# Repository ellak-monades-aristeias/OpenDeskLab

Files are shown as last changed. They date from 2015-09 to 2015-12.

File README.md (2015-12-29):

# OpenDeskLab




OpenDeskLab continuous documentation can be found in [Read the Docs](https://opendesklab.readthedocs.org/)

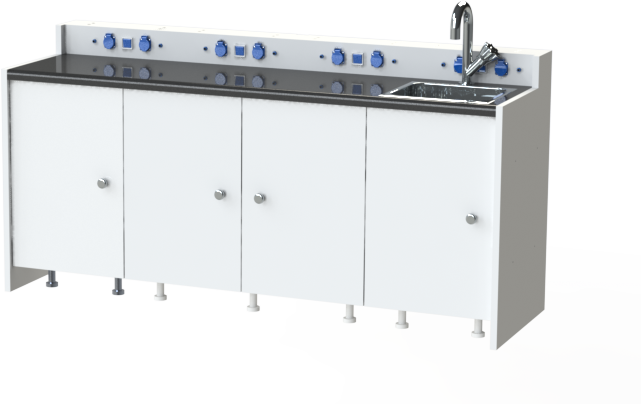
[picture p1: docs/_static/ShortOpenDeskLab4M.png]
OpenDeskLab


## Σύντομη Περιγραφή

Τα γραφεία εργαστηρίων σχολικών μονάδων φυσικών επιστημών είναι μια ειδική κατηγορία πάγκων εργασίας που έχουν στόχο την εξυπηρέτηση της διεξαγωγής των εργαστηρίων φυσικής, χημείας, βιολογιάς, γεωλογίας και γεωγραφίας. Οι ανάγκες των εργαστηριών αυτών διαφέρουν σημαντικά, αλλά έχουν κοινό γνώμονα ότι στοχεύουν να προστατεύουν τους ανήλικους μαθητές από ατυχήματα που μπορεί να συμβούν κατά την διεξαγωγή των πειραμάτων. Ταυτόχρονα, παρέχουν ευκολίες για την πραγματοποίηση των εργαστηρίων, όπως η ασφαλής παροχή ηλεκτρικού ρεύματος (εναλλασσόμενου και συνεχούς), η παροχή και αποχέτευση ρευστών (αέριων και υγρών) καθώς και η εύκολη πρόσβαση σε συστήματα ασφαλείας (πυρόσβεση/ηλεκτρικές ασφάλειες).

## Τεχνικά στοιχεία πρότασης
Το OpenDeskLab αποτελεί μία πρόταση για ένα παραμετροποιήσιμο γραφείο εργαστηρίων που μπορεί να διαμορφωθεί κατάλληλα ανάλογα με τις (εργαστηριακές) απαιτήσεις και τον διαθέσιμο χώρο. Το OpenDeskLab είναι σύμφωνο με τους κανονισμούς ασφαλείας όπως ορίζονται από τους Ελληνικούς κανονισμούς, και με υψηλή ποιότητα ώστε να εξυπηρετεί τις ανάγκες χωρίς να απαιτεί υψηλό κόστος συντήρησης. Ταυτόχρονα, θα χρησιμοποιεί φιλικά προς το περιβάλλον υλικά και θα διατηρεί χαμηλό κόστος κατασκευής, βοηθώντας την εξάπλωση του σε όλα τα δημόσια και ιδιωτικά εκπαιδευτήρια, φέρνοντας την πειραματική διδασκαλία κοντά σε όλους τους μαθητές.

Το OpenDeskLab διαθέτει

* __Αρθρωτή δομή,__ ώστε να διατηρείται το κόστος κατασκευής το χαμηλότερο δυνατό για τις ανάγκες που χρειάζονται
* __Παραμετροποιήσιμες διαστάσεις,__ ώστε να εκμεταλεύεται βέλτιστα τον χώρο του εργαστηρίου
* __Παροχή ηλεκτρικού ρεύματος,__ για την εύκολη διεξαγωγή πειραμάτων που χρειάζονται ηλεκτρική ισχύ
* __Παροχή και αποχέτευση νερού,__ για την εύκολη πρόσβαση στον καλύτερο διαλύτη της φύσης
* __Παροχή και αποχέτευση αέρα,__ για την εύκολη πρόσβαση σε αέρα υπό πίεση
* __Αποθηκευτικούς χώρους,__ για την φύλαξη των επικίνδυνων υλικών
* __Εξαερισμό,__ για την αποχέτευση αέριων παράγωγων από την αίθουσα
* __Ασφάλεια,__ για την προστασία των μαθητών μέσω πυρόσβεσης, ηλεκτρικών ρελέ, και χημικά ανενεργών υλικών κατασκευής

Συγκεκριμένα, το OpenDeskLab δίνει την δυνατότητα στους κατασκευαστές του να το παραμετροποιήσουν πλήρως στις ανάγκες τους, είτε αυτές είναι ο χώρος διεξαγωγής πειραμάτων ενός σχολείου είτε ένας εργαστηριακός χώρος ενός [hackerspace](https://en.wikipedia.org/wiki/Hackerspace) ή [fablab](https://en.wikipedia.org/wiki/Fab_lab). Η αρθρωτή δομή του επιτρέπει να δομηθεί είτε ως ηλεκτρολογικός πάγκος, είτε ως χημικός πάγκος, είτε ως πάγκος γενικών εργασιών. Σαν ηλεκτρολογικός πάγκος, διαθέτει παροχές συνεχούς και εναλλασσόμενου ρεύματος αλλά και εύκολες συνδέσεις μετρητικών (παλμογράφων/πολυμέτρων), με ηλεκτρολογικές ασφάλειες και ρελέ. Σαν χημικός πάγκος, διαθέτει παροχή αέρα και νερού, αποχέτευση, κάδο αποβλήτων και αποθηκευτικό χώρο για επικίνδυνα υλικά και υλικά που φθείρονται από την έκθεση σε φωτισμό. Τέλος, σαν πάγκος γενικής χρήσης παρέχει φωτισμό, παροχή ισχύος για εργαλεία, παροχή πεπιεσμένου αέρα, προστασία μέσω πυρόσβεσης και εξαερισμού για την σκόνη και τον καπνό (από κολλήσεις ή άλλες διεργασίες).

### Καινοτομία, ανάλογες λύσεις και χρησιμότητα
Στην αγορά αυτή την στιγμή υπάρχουν πολλές εταιρίες που παρέχουν έτοιμες ή και προσαρμοσμένες λύσεις για εργαστηριακά γραφεία σχολικών εγκαταστάσεων \[[vasileiou](http://www.basileiou.com/), [psa](http://www.psalaboratoryfurniture.com/), [rizos](http://rizos.com.gr/epipla-ergastiriou-epiplwsi.html), [ecofarm](http://www.ecofarm.net/plist.php?cat_id=24), [kertus](http://www.kertus.gr/pharmacists/index.php?option=com_k2&view=itemlist&task=category&id=80:%CE%AD%CF%80%CE%B9%CF%80%CE%BB%CE%B1-%CE%B5%CF%81%CE%B3%CE%B1%CF%83%CF%84%CE%B7%CF%81%CE%AF%CE%BF%CF%85&lang=el)\]. Το κόστος αυτών όμως είναι ιδιαιτέρως αυξημένο, καθώς αναφέρονται σε ένα προϊόν που έχει περιορισμένο κοινό και αυξημένες απαιτήσεις ασφαλείας. Τα μεγαλύτερα ιδιωτικά εκπαιδευτήρια της Ελλάδας, δεν χρησιμοποιούν γραφεία ειδικά σχεδιασμένα για την διεξαγωγή εργαστηρίων φυσικών επιστημών, καθώς ακόμα και για αυτά, το κόστος αγοράς τους είναι απαγορευτικό. Στα δημόσια εκπαιδευτήρια, από την άλλη, οι εργαστηριακοί χώροι που διατίθενται για τους μαθητές είναι λιγότεροι από 100 για όλη την χώρα, πράγμα που αναλογεί σε πολύ λίγα λεπτά εργαστηριακού χρόνου για κάθε μαθητή.

Το OpenDeskLab είναι το πρώτο ανοιχτό γραφείο εργαστηριακών πειραμάτων, και έχει στόχο να αποτελέσει το έναυσμα ώστε να διαδοθεί η τεχνογνωσία για τον εξοπλισμό και την κατασκευή ανοιχτών εργαστηρίων σε όλο τον κόσμο, τηρώντας τα διεθνή πρότυπα ασφαλείας. 

### Κοινωνικά Οφέλη
Με κύριο στόχο τον περιορισμό του κόστους λειτουργίας αλλά και του κόστους ανέγερσης νέων σχολικών μονάδων, δεδομένης της δύσκολης οικονομικής κατάστασης της χώρας, το Υπουργείο Παιδείας το 2012 όρισε την δημιουργία των ΕΚΦΕ (Εργαστηριακά Κέντρα Φυσικών Επιστημών). Τα ΕΚΦΕ έχουν στόχο την τεχνική και οργανωτική υποστήριξη της εργαστηριακής διδασκαλίας των φυσικών μαθημάτων \[[ΦΕΚ](http://edu.klimaka.gr/arxeio/nomothesia-fek/fek-2314-2012-epilogh-ypevthynoi-scholikes-drasthriothtes-klimaka.pdf)\]. Σε κάθε Διεύθυνση Δευτεροβάθμιας εκπαίδευσης λειτουργεί ένα τουλάχιστον ΕΚΦΕ, ενώ στις πυκνοκατοικημένες περιοχές λειτουργούν περισσότερα ΕΚΦΕ με στόχο να εξυπηρετούν καλύτερα τα πολλά σχολεία της περιοχής. Συνολικά στην Ελλάδα λειτουργούν 78 ΕΚΦΕ, εκ των οποιών τα 15 βρίσκονται στον νομό Αττικής ενώ σε πολλούς νομούς της Ελλάδας υπάρχει μόνο ένα ΕΚΦΕ για να εξυπηρετεί όλα τα σχολεία που συχνά βρίσκονται απομακρυσμένα από αυτό.

Το πάγιο κόστος ενός Εργαστηριακού Κέντρου Φυσικών Επιστημών είναι υψηλό, καθώς απαιτεί εργαστηριακό εξοπλισμό υψηλού κόστους, ηλεκτρονικούς υπολογιστές και ειδικές πειραματικές διατάξεις. Το κόστος χρήσης από την άλλη αποτελείται από το κόστος των εργαζομένων καθώς και τα αναλώσιμα απαραίτητα για την διεξαγωγή των εργαστηρίων. Τέλος, πρέπει να συμπεριληφθεί και το κόστος συντήρησης των εγκαταστάσεων, ηλεκτροδότησης, τηλεπικοινωνιών και υδροδότησης.

Με την ανάπτυξη του OpenDeskLab, δύναται στα σχολεία να διαθέτουν δικό τους εργαστηριακό χώρο, με χαμηλό κόστος χωρίς να χρειάζεται να συντηρούνται τα ΕΚΦΕ και χωρίς να αυξάνεται το κόστος χρήσης προς το Υπουργείο Παιδείας. Όλα τα ιδρύματα δευτεροβάθμιας εκπαίδευσης έχουν εκπαιδευμένο προσωπικό για την διεξαγωγή πειραμάτων (καθηγητές φυσίκης, χημείας κλπ). Επίσης, το κόστος των αναλωσίμων που απαιτούνται για την πραγματοποίηση των εργαστηρίων συνολικά δεν αλλάζει, καθώς θα διεξάγεται ο ίδιος αριθμός εργαστηριακών ασκήσεων.

## Σε ποίους απευθύνεται

### Κοινότητες Χρηστών
Το OpenDeskLab απευθύνεται σε όλους τους εργαστηριακούς χώρους, είτε πρόκειται για σχολικές εγκαταστάσεις είτε ανοιχτές κοινότητες makers, όπως hackerspaces, makerlabs, fablabs κλπ. 

### Κοινότητες Κατασκευαστών
Οι κατασκευαστές που ενδιαφέρονται να αναπτύξουν/επεκτείνουν το έργο, προτείνεται να έχουν γνώσεις πάνω στην κατασκευή επίπλων ή τον μηχανολογικό σχεδιασμό, πρόσβαση σε κάποιο ανοιχτό ή κλειστό πρόγραμμα τρισδιάστατου σχεδιασμού και γνώσεις της πλατφόρμας Sphinx (σύνταξη κειμένου σε Restructured Text).

Βεβαίως, ενθαρρύνονται όλες οι προτάσεις για περαιτέρω βελτίωση του έργου ακόμα και από απλούς χρήστες που παρατήρησαν κάποια έλλειψη ή κάποια δυσλειτουργία του OpenDeskLab, με την χρήση των issues.

## Κόστος

Όσον αφορά το κόστος, το OpenDeskLab μπορεί να παραμετροποιηθεί με πολλούς διαφορετικούς τρόπους, μεταβάλλοντας σημαντικά το τελικό κόστος του ανά μονάδα. Το πιο ακριβό κομμάτι του είναι το [Hazardous Materials Cabinet](https://opendesklab.readthedocs.org/en/latest/include/parts/hazardous_materials_cabinet.html#bill-of-materials), που στοιχίζει περίπου 226 euro. Από την άλλη το [Drawer Cabinet](https://opendesklab.readthedocs.org/en/a/include/parts/drawer_cabinet.html#bill-of-materials) κοστίζει μόλις 56 euro, το [Double Cabinet](https://opendesklab.readthedocs.org/en/latest/include/parts/double_cabinet.html#bill-of-materials) μόνο 57 euro και το [Single Cabinet](https://opendesklab.readthedocs.org/en/latest/include/parts/single_cabinet.html#bill-of-materials) μόλις 40 euro. Τα επιπρόσθετα κομμάτια που είναι απαραίτητα για το OpenDeskLab κοστίζουν σαφώς λιγότερο, για παράδειγμα το [Short Desk Back](https://opendesklab.readthedocs.org/en/latest/include/parts/desk_back.html#id3) ξεκινάει περίπου στα 39 euro και μπορεί να φτάσει τα 82 euro για την έκδοση Tall, ενώ τα [Side Panels](https://opendesklab.readthedocs.org/en/latest/include/parts/desk_side.html#id3) κοστίζουν 22 ή 33 euro το ζευγάρι, για την short ή την tall έκδοση αντίστοιχα. 

Τα πιο ακριβά απαραίτητα κομμάτια του OpenDeskLab είναι τα ηλεκτρικά και πνευματικά φις του [Cable Routing](https://opendesklab.readthedocs.org/en/latest/include/parts/cable_routing.html#bill-of-materials), που ξεκινούν από τα 78 euro και μπορούν να φτάσουν τα 131 euros. Το κομμάτι [Worktop](https://opendesklab.readthedocs.org/en/latest/include/parts/worktop.html#bill-of-materials) από την άλλη πλευρά κοστίζει από 33 euro μέχρι περίπου 56 euro έκαστο (για διαφορετικές διαστάσεις).

Τα ανωτέρω κόστη είναι υπολογισμένα σύμφωνα με τις τιμές των πρώτων υλών, και ενδέχεται να διαφέρουν στην περίπτωση που η διαμόρφωση της κατασκευής (ή η ποσότητα των κατασκευαζόμενων γραφείων) αφήνει μεγάλο περίσσευμα πρώτης ύλης ανεκμετάλευτο (φύλλα μελαμίνης, πάγκος εργασίας, βίδες κλπ).

Για την κατασκευή των φύλλων μελαμίνης χρείαζεται πρόσβαση σε εργαλειομηχανή κατεργασίας ξύλου αριθμητικού ελέγχου. Για την συναρμολόγηση του γραφείου, ανάλογα με την διαμόρφωση του, χρειάζονται ελάχιστα εργαλεία, θεωρώντας ότι τα φύλλα είναι ήδη επεξεργασμένα και οι οπές γίνανε από την εργαλειομηχανή σε προηγούμενο στάδιο.

## Χρονοδιάγραμμα
| Ημερομηνίες	| Διάρκεια | Περιγραφή Εργασιών 																		|
|---------------|----------|--------------------------------------------------------------------------------------------|
| 17/09 - 21/09 | 3 Ημ.    | Συγκέντρωση προδιαγραφών και απαιτήσεων, μελέτη των κανονισμών ασφαλείας 					|
| 22/09 - 02/10 | 9 Ημ.    | Αναλυτικός σχεδιασμός, μελέτη εργονομίας και λειτουργικότητας, σχεδιασμός για συναρμολόγηση|
| 05/10 - 09/10 | 5 Ημ.    | Κοστολόγιση και πίνακας υλικών (Bill of Materials) 										|
| 12/10 - 15/10 | 4 Ημ.  | Συγγραφή της τεκμηρίωσης και αναλυτικών οδηγιών κατασκευής 								    |

## Παραδοτέα
Στα πλαίσια των αρχών του ανοιχτού υλισμικού, τα παραδοτέα της πρότασης θα διατεθούν με άδεια Creative Commons. Ταυτόχρονα, όπου γίνεται θα προτιμηθούν τα ανοιχτά πρότυπα, χωρίς όμως να αποτελέσουν περιοριστικό παράγοντα για την κατασκευή και την εξάπλωση του OpenDeskLab. Με βασικό κριτήριο την ευκολία κατασκευής αλλά και την συμβατότητα με τα καθιερωμένα προγράμματα σχεδιασμού, τα αρχεία θα διατεθούν σε μορφή [STEP](https://en.wikipedia.org/wiki/ISO_10303-21), [DWG](https://en.wikipedia.org/wiki/.dwg) και δισδιάστατου [DXF](https://en.wikipedia.org/wiki/AutoCAD_DXF) για να είναι εύκολα κατασκευάσιμα από μηχανές αριθμητικού ελέγχου (CNC), αλλά και σε μορφή διαστασιολογημένων PDF για να κατασκευάζεται με απλά ηλεκτρικά εργαλεία χωρίς να απαιτείται πρόσβαση σε ακριβές εργαλειομηχανές.

| Τίτλος Παραδοτέου 													| Url     |
|-----------------------------------------------------------------------|---------|
| Τεχνική αναφορά με τις προδιαγραφές και τους κανονισμούς ασφαλείας 	| [source](https://github.com/ellak-monades-aristeias/OpenDeskLab/blob/master/docs/include/specifications.rst), [html](https://opendesklab.readthedocs.org/en/latest/include/specifications.html)  |
| Παραμετρικά σχέδια κατασκευής και εικόνες, μελέτη εργονομίας 			| [folder](https://github.com/ellak-monades-aristeias/OpenDeskLab/tree/master/docs/_static), [html](https://opendesklab.readthedocs.org/en/latest/include/modules.html#module-list), [grabcad](https://grabcad.com/library/opendesklab-2) |
| Σχέδια για συναρμολόγηση												| [videos](https://github.com/ellak-monades-aristeias/OpenDeskLab/tree/master/docs/_static), [OpenDeskLab html](https://opendesklab.readthedocs.org/en/latest/include/modules.html), [Cable Routing html](https://opendesklab.readthedocs.org/en/latest/include/parts/cable_routing.html#assembly-procedure), [Double Cabinet html](https://opendesklab.readthedocs.org/en/latest/include/parts/double_cabinet.html#assembly-procedure), [Drawer Cabinet html](https://opendesklab.readthedocs.org/en/latest/include/parts/drawer_cabinet.html#assembly-procedure), [Hazardous Materials Cabinet html](https://opendesklab.readthedocs.org/en/latest/include/parts/hazardous_materials_cabinet.html#assembly-procedure), [Sink Cabinet html](https://opendesklab.readthedocs.org/en/latest/include/parts/sink_cabinet.html#assembly-procedure) |
| Τεκμηρίωση και τεχνική αναφορά οδηγιών κατασκευής						| [Read The Docs](https://opendesklab.readthedocs.org/en/latest/index.html) |

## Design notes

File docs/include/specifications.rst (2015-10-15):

=============================
Specifications & Requirements
=============================

According to the rules and regulations of the EU_ and most International Standards committees, there are some safety rules that must be taken into account for manufacturing laboratory equipment. However, although OpenDeskLab is designed according to those rules, it must be noted that the authors and creators of OpenDeskLab are **not** eligible for any kind of damage that may happen while building or using the desk. A laboratory that is used in professional environments **must** be certified by an authorized person, and OpenDeskLab is neither certified nor can fullfil all the regulations of every standard in the world.

.. warning::

    OpenDeskLab is not certified for professional use. The authors are not eligible for any damage that may occur while building or using the product.

:index:`Safety`
---------------

- Central ventilation is required in laboratory facilities
- Water tap within 15 meters or 10 seconds of the users
- Chemical storage must have edges protected for spillage
- Flammable materials must be stored in UL/NFPA certified storage areas
- Acids and bases must be stored separately
- Compressed air canisters must me fixed securely with fire resistant strands
- Toxic wastes must be handled according to specific regulations
- All storage areas must be clearly signed
- Labels must be placed for

    - Water
    - Electricity
    - Chemicals
    - Flammables
    - Acids/Bases

:index:`Specifications`
-----------------------

OpenDeskLab is comprised of the following modules:

- :doc:`parts/cable_routing`
- :doc:`parts/desk_back`
- :doc:`parts/desk_side`
- :doc:`parts/double_cabinet`
- :doc:`parts/drawer_cabinet`
- :doc:`parts/hazardous_materials_cabinet`
- :doc:`parts/lighting`
- :doc:`parts/single_cabinet`
- :doc:`parts/sink_cabinet`
- :doc:`parts/worktop`

These can be combined in any desirable way to formulate a -- three, four or five module wide -- self-contained laboratory desk. 

:index:`Materials`
------------------

    .. tabularcolumns:: |c|c|
    .. table:: 

        ======================= ==================
         **OpenDeskLab Materials**
        ------------------------------------------
        Melamine                Electric Plug
        Plywood                 Electric Cable
        Cam Lock                Pneumatic Coupling
        Cam Bolt                Pneumatic Tubing
        Wooden Dowel Pin        Sink
        Concealed Hinge         Water Tap
        Hinge Mounting Plate    Hydraulic Hose
        Plastic Adjustable Leg  Plastic Tube
        Metal Adjustable Leg    Silicone Caulk
        Knob                    LED Lighting
        Electric Switch         Insulating Tape
        Intumescent Paint       
        ======================= ==================

.. _EU: https://en.wikipedia.org/wiki/European_Union

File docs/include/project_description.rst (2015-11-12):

============================
Project :index:`Description`
============================



OpenDeskLab aims at creating an open design for laboratory desks that is

- Modular structure
- Reconfigurable dimensions
- Safe
- Easy to build
- Low cost
- Highly functional

The material used for the structure of is mostly melamine boards, that can be precut by any CNC supplier to the given dimensions. The assembly of an OpenDeskLab is designed so as to require only the basic of the tools, such as a Pozidriv screwdriver. The desk itself can be configured in many different ways, and the materials as well as the aesthetics can be customized according to the owners taste.

All the materials chosen for the OpenDeskLab (and their respective sockets) are dimensioned according to the International standards and can be sourced online or in many local stores. The desk can be assembled easily, following the instructive videos provided for each component. Various components are provided, although anyone can design his own component to pair with the already developed ones.

OpenDeskLab can be built in three, four and five module variants. The builder may choose the modules that will form his desk according to his needs, and the modular design will accommodate every customization (with some minor limitations) possible. 

:index:`Applications`
---------------------

The main audience that OpenDeskLab targets are high school laboratories and home/diy/hackerspace/fablab places. Due to its' modular nature, OpenDeskLab can be used in a variety of applications, including (but not limited to) electrical, chemical and general use workbenches. It can provide electrical as well as gas connections, water supply and drain and of course ventilation. A hazardous materials storage is also provided that is the only fully self-contained module that can provide a safe storage for chemicals and flammables.  

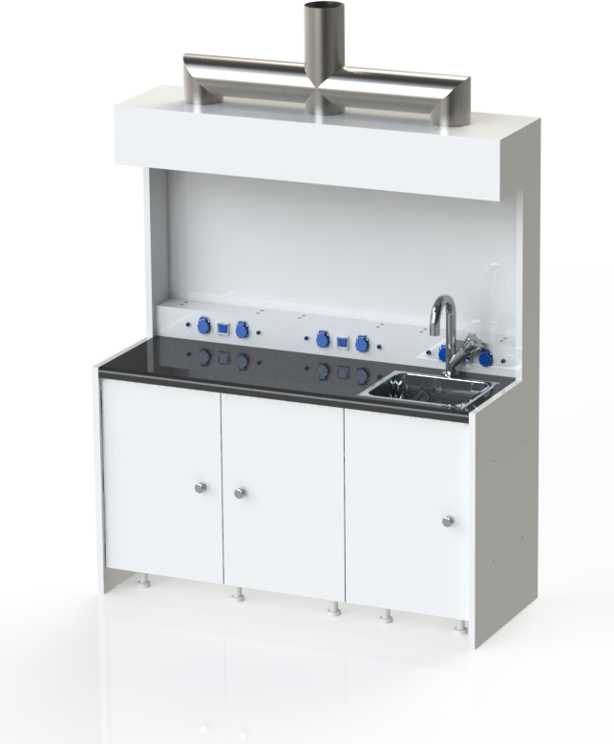
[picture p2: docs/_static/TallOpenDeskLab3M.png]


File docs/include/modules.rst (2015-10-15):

============================
:index:`Modules`
============================

OpenDeskLab is comprised of different modules that can be assembled following some basic guidelines.

Assembly Procedure
~~~~~~~~~~~~~~~~~~

The modules are assembled together using M6 connecting screws through the four holes that exist in every module.

.. raw:: html 

   <video src="../_static/OpenDeskLab3M.ogv" width="696" type="video/ogg" controls="controls">
   Your browser does not support the video tag.
   </video>

Drawings
~~~~~~~~

:download:`Tall OpenDeskLab </_static/OpenDeskLab3M.pdf>`

:download:`Short OpenDeskLab </_static/OpenDeskLabShort4M.pdf>`

+-------------------------------------+--------------------------------------+--------------------------------------+
| OpenDeskLab modules with bakelite doors                                                                           |
+=====================================+======================================+======================================+
| 
|                                     |                                      |                                      |
| (a) :doc:`parts/single_cabinet`     | (b) :doc:`parts/double_cabinet`      | (c) :doc:`parts/drawer_cabinet`      |
+-------------------------------------+--------------------------------------+--------------------------------------+

Module List
~~~~~~~~~~~

.. toctree::
   :maxdepth: 1
   
   parts/cable_routing
   parts/desk_back
   parts/desk_side
   parts/double_cabinet
   parts/drawer_cabinet
   parts/hazardous_materials_cabinet
   parts/lighting
   parts/single_cabinet
   parts/sink_cabinet
   parts/worktop

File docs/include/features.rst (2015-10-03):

=================
:index:`Features`
=================

.. toctree::
   
   parts/single_cabinet
   parts/double_cabinet
   parts/drawer_cabinet
   parts/sink_cabinet
   parts/hazardous_materials_cabinet
   parts/cable_routing
   parts/top_mount_lighting
   parts/top_mount_ventilation
   parts/worktop

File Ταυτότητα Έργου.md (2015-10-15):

# Ταυτότητα Έργου

OpenDeskLab

## Περιγραφή του Έργου
Το OpenDeskLab αποτελεί μία πρόταση για ένα παραμετροποιήσιμο γραφείο εργαστηρίων που μπορεί να διαμορφωθεί κατάλληλα ανάλογα με τις (εργαστηριακές) απαιτήσεις και τον διαθέσιμο χώρο. Το OpenDeskLab είναι σύμφωνο με τους κανονισμούς ασφαλείας όπως ορίζονται από τους Ελληνικούς κανονισμούς, και με υψηλή ποιότητα ώστε να εξυπηρετεί τις ανάγκες χωρίς να απαιτεί υψηλό κόστος συντήρησης. Ταυτόχρονα, χρησιμοποιεί φιλικά προς το περιβάλλον υλικά και διατηρεί χαμηλό κόστος κατασκευής, βοηθώντας την εξάπλωση του σε όλα τα δημόσια και ιδιωτικά εκπαιδευτήρια, φέρνοντας την πειραματική διδασκαλία κοντά σε όλους τους μαθητές.

Η αρθρωτή δομή του επιτρέπει να δομηθεί είτε ως ηλεκτρολογικός πάγκος, είτε ως χημικός πάγκος, είτε ως πάγκος γενικών εργασιών. Σαν ηλεκτρολογικός πάγκος, διαθέτει παροχές συνεχούς και εναλλασσόμενου ρεύματος. Σαν χημικός πάγκος, διαθέτει παροχή αέρα και νερού, αποχέτευση, κάδο αποβλήτων και αποθηκευτικό χώρο για επικίνδυνα υλικά και υλικά που φθείρονται από την έκθεση σε φωτισμό. Τέλος, σαν πάγκος γενικής χρήσης παρέχει φωτισμό, παροχή ισχύος για εργαλεία, παροχή πεπιεσμένου αέρα και εξαερισμού για την σκόνη και τον καπνό (από κολλήσεις ή άλλες διεργασίες).

## Χρησιμότητα
Τα μεγαλύτερα ιδιωτικά εκπαιδευτήρια της Ελλάδας, δεν χρησιμοποιούν γραφεία ειδικά σχεδιασμένα για την διεξαγωγή εργαστηρίων φυσικών επιστημών, καθώς ακόμα και για αυτά, το κόστος αγοράς τους είναι απαγορευτικό. Στα δημόσια εκπαιδευτήρια, από την άλλη, οι εργαστηριακοί χώροι που διατίθενται για τους μαθητές είναι λιγότεροι από 100 για όλη την χώρα, πράγμα που αναλογεί σε πολύ λίγα λεπτά εργαστηριακού χρόνου για κάθε μαθητή.

Το OpenDeskLab είναι το πρώτο ανοιχτό γραφείο εργαστηριακών πειραμάτων, και έχει στόχο να αποτελέσει το έναυσμα ώστε να διαδοθεί η τεχνογνωσία για τον εξοπλισμό και την κατασκευή ανοιχτών εργαστηρίων σε όλο τον κόσμο, τηρώντας τα διεθνή πρότυπα ασφαλείας. 

## Ελάχιστες Απαιτήσεις
Το OpenDeskLab χρησιμοποιεί σαν πρώτη ύλη μελαμίνη πάχους 18 και 25 χιλιοστών. Για το μεγαλύτερο μέρος των συνδέσμων του χρησιμοποιεί έκκεντρα φεράμια που επιτρέπουν την εύκολη συναρμολόγηση και αποσυναρμολόγηση του πάγκου και των αποθηκευτικών χώρων χωρίς την χρήση πολύπλοκων εργαλείων.

Για την τεκμηρίωση όλου του έργου χρησιμοποιήθηκε η πλατφόρμα Sphinx, και το σύστημα συνεχούς τεκμηρίωσης [Read the Docs](http://www.readthedocs.org). Τα σχέδια υλοποιήθηκαν στο [SolidWorks 2016](http://www.solidworks.com), ενώ διατίθενται ελεύθερα μέσω της πλατφόρμας [GrabCAD](http://www.grabcad.com), μέσα από την οποία μπορεί κάποιος να τα μεταφορτώσει σε οποιοδήποτε ουδέτερο πρότυπο CAD αρχείων (STEP, IGES, STL).

## Αποθετήριο
Το αποθετήριο μπορεί να βρεθεί στο [github](https://github.com/ellak-monades-aristeias/OpenDeskLab), η τεκμηρίωση του στο [Read the Docs](http://opendesklab.readthedocs.org) ενώ τα τρισδιάστατα μοντέλα CAD στο [GrabCAD](http://www.grabcad.com/library/opendesklab-2) υπό την άδεια χρήσης [CC BY-SA 4.0](https://creativecommons.org/licenses/by-sa/4.0/).

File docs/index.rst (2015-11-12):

.. OpenDeskLab documentation master file, created by
   sphinx-quickstart on Wed Sep 30 19:01:20 2015.
   You can adapt this file completely to your liking, but it should at least
   contain the root `toctree` directive.

=======================================
Welcome to OpenDeskLab's documentation!
=======================================

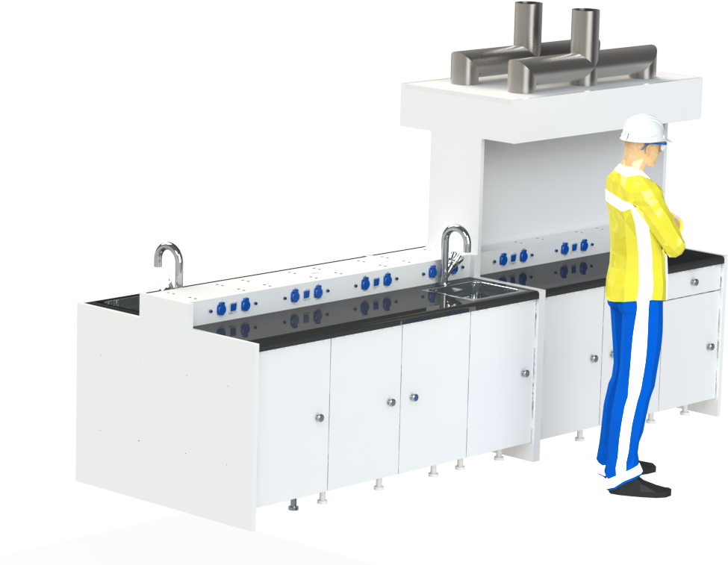
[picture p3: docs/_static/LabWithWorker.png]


.. toctree::
   :maxdepth: 2
   :glob:

      Project Description <include/project_description>
      Specifications <include/specifications>
      Modules <include/modules>
      Open Data <include/open_data>
      Acknowledgments <include/acknowledgments>

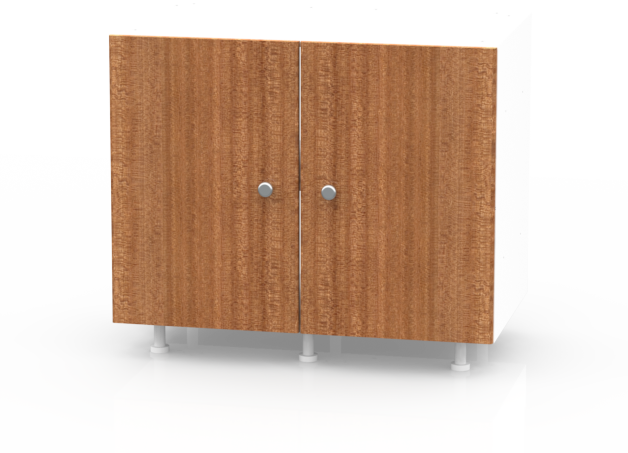
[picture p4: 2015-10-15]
docs/_static/wood/double.png

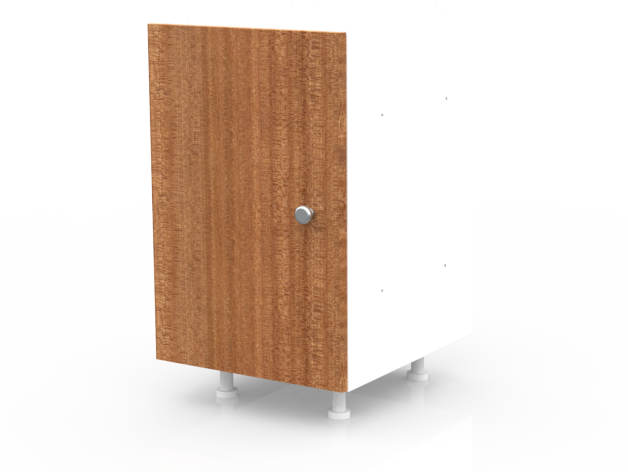
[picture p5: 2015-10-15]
docs/_static/wood/single.png

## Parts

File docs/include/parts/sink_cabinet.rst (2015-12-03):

:index:`Sink Cabinet`
---------------------

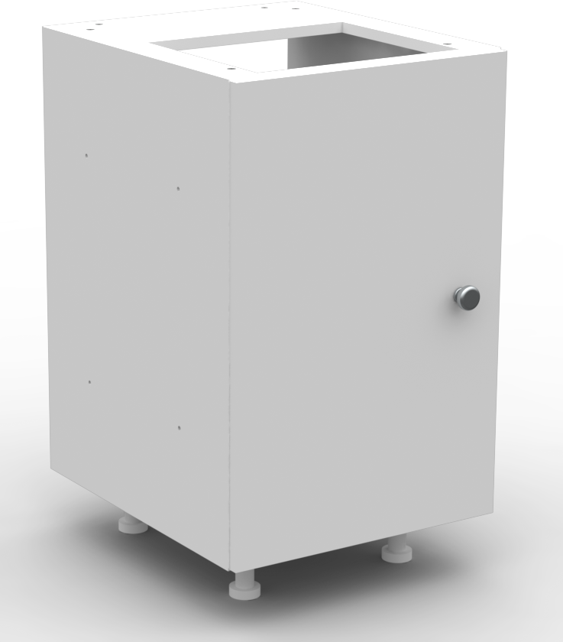
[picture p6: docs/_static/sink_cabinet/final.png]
sink cabinet


The sink cabinet is very similar to the :doc:`single_cabinet` module, however, the top shelf has a precut hole for the installation of the sink and the tap.

Although there are standard sizes for sinks and taps in the industry, most manufacturers tend to not follow them, for design reasons. This cabinet is designed for a 375x317 sink, which is a small standard sink size, however, in the case were the builder wants to use different sink size, he can choose to cut the hole using a jigsaw.

.. important::

    Tools Needed:
     - Pozidriv Screwdriver
     - Electric Screwdriver for the four plastic legs
     - Wrench
     - Jigsaw (Optional)

Assembly Procedure
~~~~~~~~~~~~~~~~~~

The assembly procedure is very simple, first you assemble the two side panels using the Cam Bolts and the Wooden Dowel Pins, and then you mount the Hinge Mounting Plates on the left or right side panel, according to your preference. (Mind there are fewer holes in the sink side panels)

.. raw:: html 

   <video src="../../_static/side_panel_assembly.ogv" width="696" type="video/ogg" controls="controls">
   Your browser does not support the video tag.
   </video>

Then you create the door assembly by mounting the Concealed Hinges with the provided screws (3.5mm x 16mm) and lastly you screw in the Knob.

.. raw:: html 

   <video src="../../_static/door_assembly.ogv" width="696" type="video/ogg" controls="controls">
   Your browser does not support the video tag.
   </video>   

Lastly you assemble them all together. The sink must be installed **after** the worktop is placed.

.. raw:: html 

   <video src="../../_static/sink_cabinet/Sink_Cabinet.ogv" width="696" type="video/ogg" controls="controls">
   Your browser does not support the video tag.
   </video>

Drawings
~~~~~~~~

:download:`Shelf </_static/single_cabinet/Melamine_Shelf.pdf>`

:download:`Top </_static/sink_cabinet/Sink_Melamine_Top.pdf>`

:download:`Side </_static/sink_cabinet/Sink_Melamine_Side.pdf>`

:download:`Sink Cabinet </_static/sink_cabinet/Sink_Cabinet.pdf>`

Bill of Materials
~~~~~~~~~~~~~~~~~

   .. tabularcolumns:: |l|c|c|c|
   .. table::

      +------------------------------------+----------+-----------+-------------+
      | Sink Cabinet - Bill of Materials                                        |
      +------------------------------------+----------+-----------+-------------+
      | Item                               | Quantity | Price/Pcs | Total Price |
      +====================================+==========+===========+=============+
      | Cam Lock 15mm x 12.5mm             |    12    |    0.148€ |      1.776€ |
      +------------------------------------+----------+-----------+-------------+
      | Cam Bolt 6mm x 45.5mm              |     8    |    0.880€ |      7.040€ |
      +------------------------------------+----------+-----------+-------------+
      | Wooden Dowel Pin 8mm x 30mm        |    12    |    0.029€ |      0.348€ |
      +------------------------------------+----------+-----------+-------------+
      | Concealed Hinge (9mm Overlay)      |     2    |    1.690€ |      3.380€ |
      +------------------------------------+----------+-----------+-------------+
      | Hinge Mounting Plate               |     2    |    0.980€ |      1.960€ |
      +------------------------------------+----------+-----------+-------------+
      | Plastic Adjustable Legs 100mm      |     4    |    0.750€ |      3.000€ |
      +------------------------------------+----------+-----------+-------------+
      | M6 x 40 Connecting Screws          |     4    |    0.753€ |      3.012€ |
      +------------------------------------+----------+-----------+-------------+
      | Melamine 18mm                      |  1.750   | 6.718€/m2 |     11.759€ |
      +------------------------------------+----------+-----------+-------------+
      | Door Knob                          |     1    |    1.080€ |      1.080€ |
      +------------------------------------+----------+-----------+-------------+
      | **Total Cost**                                            |     33.355€ |
      +------------------------------------+----------+-----------+-------------+

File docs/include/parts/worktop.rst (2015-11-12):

:index:`Worktop`
----------------

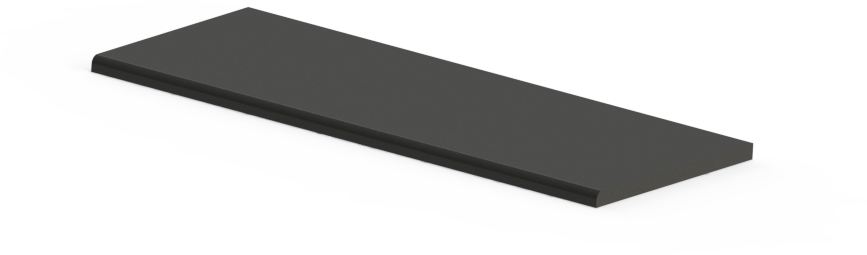
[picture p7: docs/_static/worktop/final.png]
worktop


.. important::

   Tools Needed:
    - Electric Screwdriver

Assembly Procedure
++++++++++++++++++

The worktop is assembled by simply screwing the top side of the cabinets with it, using the Pozidriv 3.5mm x 35mm screws. You open the doors of the cabinets, lie down on them and using an electric screwdriver you secure it in place.

If you have installed a sink cabinet module, you must also securely attach it to the worktop following the instructions provided by the sink.

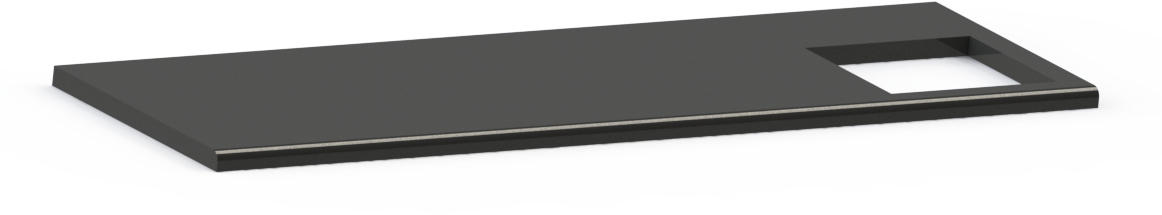
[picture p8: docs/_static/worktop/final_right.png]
worktop right


Drawings
++++++++

:download:`Worktop 3M </_static/worktop/Worktop_3M.pdf>`

:download:`Worktop Left Sink 3M </_static/worktop/Worktop_Left_Sink_3M.pdf>`

:download:`Worktop Right Sink 3M </_static/worktop/Worktop_Right_Sink_3M.pdf>`

Bill of Materials
+++++++++++++++++

   .. tabularcolumns:: |l|c|c|c|
   .. table::

      +------------------------------------+----------+-----------+-------------+
      | Worktop 3M - Bill of Materials                                          |
      +------------------------------------+----------+-----------+-------------+
      | Item                               | Quantity | Price/Pcs | Total Price |
      +====================================+==========+===========+=============+
      | Pozidriv Screws 3.5mm x 35mm       |      12  |   0.0188€ |      0.225€ |
      +------------------------------------+----------+-----------+-------------+
      | Worktop 40mm                       |     1.5  | 22.142€/m |     33.214€ |
      +------------------------------------+----------+-----------+-------------+
      | **Total Cost**                                            |     33.439€ |
      +------------------------------------+----------+-----------+-------------+

   .. tabularcolumns:: |l|c|c|c|
   .. table::

      +------------------------------------+----------+-----------+-------------+
      | Worktop 4M - Bill of Materials                                          |
      +------------------------------------+----------+-----------+-------------+
      | Item                               | Quantity | Price/Pcs | Total Price |
      +====================================+==========+===========+=============+
      | Pozidriv Screws 3.5mm x 35mm       |      16  |   0.0188€ |      0.300€ |
      +------------------------------------+----------+-----------+-------------+
      | Worktop 40mm                       |       2  | 22.142€/m |     44.285€ |
      +------------------------------------+----------+-----------+-------------+
      | **Total Cost**                                            |     44.586€ |
      +------------------------------------+----------+-----------+-------------+

   .. tabularcolumns:: |l|c|c|c|
   .. table::

      +------------------------------------+----------+-----------+-------------+
      | Worktop 5M - Bill of Materials                                          |
      +------------------------------------+----------+-----------+-------------+
      | Item                               | Quantity | Price/Pcs | Total Price |
      +====================================+==========+===========+=============+
      | Pozidriv Screws 3.5mm x 35mm       |      20  |   0.0188€ |      0.376€ |
      +------------------------------------+----------+-----------+-------------+
      | Worktop 40mm                       |     2.5  | 22.142€/m |     55.357€ |
      +------------------------------------+----------+-----------+-------------+
      | **Total Cost**                                            |     55.733€ |
      +------------------------------------+----------+-----------+-------------+

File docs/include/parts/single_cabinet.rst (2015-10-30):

:index:`Single Cabinet`
-----------------------

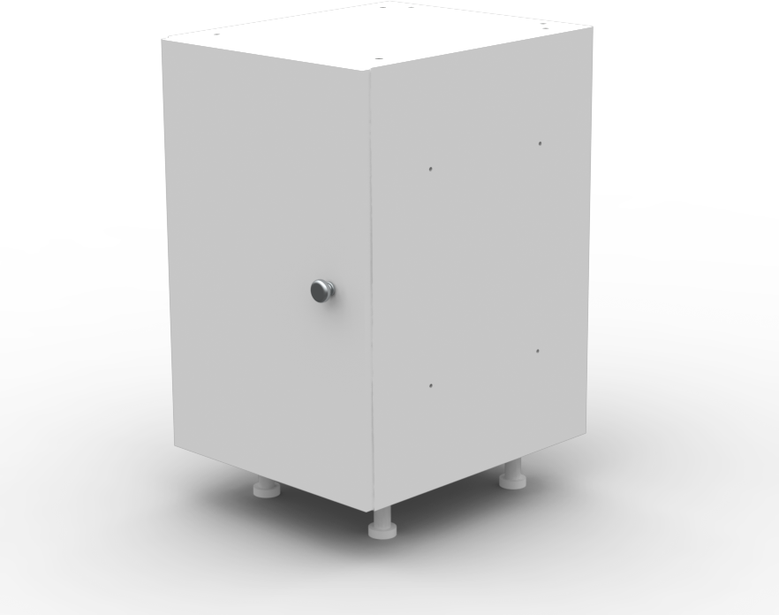
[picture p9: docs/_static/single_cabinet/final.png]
single cabinet


The single cabinet is a single module for the OpenDeskLab. It is comprised of the five melamine boards that form the frame (with the shelf) and the bakelite door that has rounded edges. 

The sides of the frame can be used to mount the door either as right swing or as left swing, with no modifications on the frame or the door itself. The hinges are standardized and all the holes can be predrilled in the CNC mill of the melamine supplier.

.. important::

    Tools Needed:
     - Pozidriv Screwdriver
     - Electric Screwdriver for the four plastic legs

Assembly Procedure
~~~~~~~~~~~~~~~~~~

The assembly procedure is very simple, first you assemble the two side panels using the Cam Bolts and the Wooden Dowel Pins, and then you mount the Hinge Mounting Plates on the left or right side panel, according to your preference.

.. raw:: html 

   <video src="../../_static/side_panel_assembly.ogv" width="696" type="video/ogg" controls="controls">
   Your browser does not support the video tag.
   </video>

Then you create the door assembly by mounting the Concealed Hinges with the provided screws (3.5mm x 16mm) and lastly you screw in the Knob.

.. raw:: html 

   <video src="../../_static/door_assembly.ogv" width="696" type="video/ogg" controls="controls">
   Your browser does not support the video tag.
   </video>

After you have assembled both sides and the door assembly you can proceed to the next step. Attach the three Melamine parts on one of the side panels and then carefully align the second side panel on the assembly. After that, screw in the Cam Locks to secure the subassembly. Lie the subassembly down and screw in the four plastic legs on the bottom of the cabinet. Lastly, attach the already assembled door on the cabinet by attaching the Concealed Hinges on their respective Hinge Mounting Plates and screw them in.

.. raw:: html 

   <video src="../../_static/single_cabinet/single_cabinet.ogv" width="696" type="video/ogg" controls="controls">
   Your browser does not support the video tag.
   </video>

Drawings
~~~~~~~~

:download:`Shelf </_static/single_cabinet/Melamine_Shelf.pdf>`

:download:`Door </_static/single_cabinet/Melamine_Door.pdf>`

:download:`Side </_static/single_cabinet/Melamine_Side.pdf>`

:download:`Single Cabinet </_static/single_cabinet/Single_Cabinet.pdf>`

Bill of Materials
~~~~~~~~~~~~~~~~~

   .. tabularcolumns:: |l|c|c|c|
   .. table::

      +------------------------------------+----------+-----------+-------------+
      | Single Cabinet - Bill of Materials                                      | 
      +------------------------------------+----------+-----------+-------------+
      | Item                               | Quantity | Price/Pcs | Total Price |
      +====================================+==========+===========+=============+
      | Cam Lock 15mm x 12.5mm             |    18    |    0.148€ |      2.664€ |
      +------------------------------------+----------+-----------+-------------+
      | Cam Bolt 6mm x 45.5mm              |    12    |    0.880€ |     10.560€ |
      +------------------------------------+----------+-----------+-------------+
      | Wooden Dowel Pin 8mm x 30mm        |    18    |    0.029€ |      0.522€ |
      +------------------------------------+----------+-----------+-------------+
      | Concealed Hinge (9mm Overlay)      |     2    |    1.690€ |      3.380€ |
      +------------------------------------+----------+-----------+-------------+
      | Hinge Mounting Plate               |     2    |    0.980€ |      1.960€ |
      +------------------------------------+----------+-----------+-------------+
      | Plastic Adjustable Legs 100mm      |     4    |    0.750€ |      3.000€ |
      +------------------------------------+----------+-----------+-------------+
      | M6 x 40 Connecting Screws          |     4    |    0.753€ |      3.012€ |
      +------------------------------------+----------+-----------+-------------+
      | Melamine 18mm                      |  2.011   | 6.718€/m2 |     13.511€ |
      +------------------------------------+----------+-----------+-------------+
      | Door Knob                          |     1    |    1.080€ |      1.080€ |
      +------------------------------------+----------+-----------+-------------+
      | **Total Cost**                                            |     39.689€ |
      +------------------------------------+----------+-----------+-------------+

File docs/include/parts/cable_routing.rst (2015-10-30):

:index:`Cable Routing`
----------------------

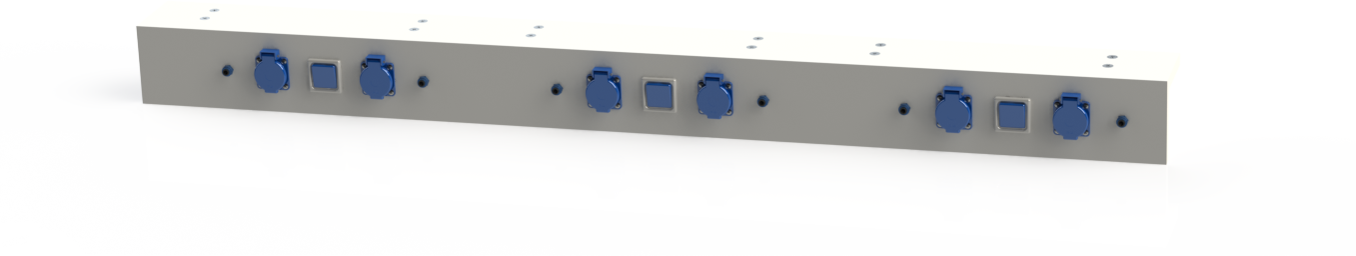
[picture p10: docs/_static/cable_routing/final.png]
cable routing


The cable routing module lies on top of the worktop, providing power and air connections for the users. The width of the melamine parts depends on the number of modules the desk will be built with.

.. important::

   Tools Needed:
    - Pozidriv Screwdriver
    - Wire Cutter
    - Tube Cutter
    - Scissors

When choosing the appropriate connections (for electricity and pneumatics) choose the appropriate plugs for your country and the correct International Protection Marking (IP Code). In laboratory environments, IP54 is the minimum requirement, and in some cases even more strict protection might be required.

   .. tabularcolumns:: |l|c|c|
   .. table::

      ======= ================= ===========================================
      IP Code Object Protection  Liquid Protection
      ======= ================= ===========================================
      0       No protection     No protection
      1       >50 mm            Dripping water
      2       >12.5 mm          Dripping water when tilted up to 15°
      3       >2.5 mm           Spraying water
      4       >1 mm             Splashing of water
      5       Dust protected    Water jets
      6       Dust tight        Powerful water jets
      6K      N/A               Powerful water jets with increased pressure
      7       N/A               Immersion up to 1 m
      8       N/A               Immersion beyond 1 m
      9k      N/A               Powerful high temperature water jets
      ======= ================= ===========================================

.. warning::

   Electrical connections must be made from an authorized electrician. The authors are not responsible for any damage or incorrect installation by the builders.

Assembly Procedure
++++++++++++++++++

The assembly of the cable routing module is perhaps the hardest part of OpenDeskLab, as it requires electrical as well as pneumatic connections. The front melamine part has predrilled holes that can be used to connect AC or DC eletric outlets or switches for the :doc:`lighting` module.

The pneumatic connectors are predrilled on either side of the electric outlets, and can be configured either as input/output connects or as outputs only.

The cable routing module provides 3 electric connections and two pneumatic connections above each module, therefore providing 9 electric and 6 pneumatic plugs for the three module-wide desk. 

Cable management for all the connections goes through the :doc:`desk_back` to their respective sources.

.. raw:: html 

   <video src="../../_static/cable_routing/Cable_Routing_3M.ogv" width="696" type="video/ogg" controls="controls">
   Your browser does not support the video tag.
   </video>

Drawings
++++++++

Drawings are provided for the three module-wide version, for the other versions nothing changes besides the overall length of the module.

:download:`Cable Routing Top 3M </_static/cable_routing/Cable_Routing_Top_3M.pdf>`

:download:`Cable Routing Front 3M </_static/cable_routing/Cable_Routing_Front_3M.pdf>`

:download:`Cable Routing </_static/cable_routing/Cable_Routing.pdf>`

Bill of Materials
+++++++++++++++++

   .. tabularcolumns:: |l|c|c|c|
   .. table::

      +------------------------------------+----------+-----------+-------------+
      | Cable Routing 3M - Bill of Materials                                    |
      +------------------------------------+----------+-----------+-------------+
      | Item                               | Quantity | Price/Pcs | Total Price |
      +====================================+==========+===========+=============+
      | Cam Lock 15mm x 12.5mm             |       12 |    0.148€ |      1.776€ |
      +------------------------------------+----------+-----------+-------------+
      | Cam Bolt 6mm x 45.5mm              |        6 |    0.880€ |      5.280€ |
      +------------------------------------+----------+-----------+-------------+
      | Wooden Dowel Pin 8mm x 30mm        |        9 |    0.029€ |      0.261€ |
      +------------------------------------+----------+-----------+-------------+
      | Melamine 18mm                      |    0.333 | 6.718€/m2 |      2.237€ |
      +------------------------------------+----------+-----------+-------------+
      | Electric Plugs                     |        6 |    2.790€ |     16.740€ |
      +------------------------------------+----------+-----------+-------------+
      | Electric Cable                     |        5 |  0.835€/m |      4.175€ |
      +------------------------------------+----------+-----------+-------------+
      | Pneumatic Coupling                 |        6 |    3.520€ |     21.120€ |
      +------------------------------------+----------+-----------+-------------+
      | Pneumatic Tubing                   |        5 |  1.191€/m |      5.955€ |
      +------------------------------------+----------+-----------+-------------+
      | Switch                             |        3 |    6.770€ |     20.310€ |
      +------------------------------------+----------+-----------+-------------+
      | Insulating Tape                    |        3 | 0.0645€/m |      0.193€ |
      +------------------------------------+----------+-----------+-------------+
      | **Total Cost**                                            |     78.048€ |
      +------------------------------------+----------+-----------+-------------+

   .. tabularcolumns:: |l|c|c|c|
   .. table::

      +------------------------------------+----------+-----------+-------------+
      | Cable Routing 4M - Bill of Materials                                    |
      +------------------------------------+----------+-----------+-------------+
      | Item                               | Quantity | Price/Pcs | Total Price |
      +====================================+==========+===========+=============+
      | Cam Lock 15mm x 12.5mm             |       16 |    0.148€ |      2.368€ |
      +------------------------------------+----------+-----------+-------------+
      | Cam Bolt 6mm x 45.5mm              |        8 |    0.880€ |      7.040€ |
      +------------------------------------+----------+-----------+-------------+
      | Wooden Dowel Pin 8mm x 30mm        |       12 |    0.029€ |      0.348€ |
      +------------------------------------+----------+-----------+-------------+
      | Melamine 18mm                      |    0.444 | 6.718€/m2 |      2.983€ |
      +------------------------------------+----------+-----------+-------------+
      | Electric Plugs                     |        8 |    2.790€ |     22.320€ |
      +------------------------------------+----------+-----------+-------------+
      | Electric Cable                     |        7 |  0.835€/m |      5.845€ |
      +------------------------------------+----------+-----------+-------------+
      | Pneumatic Coupling                 |        8 |    3.520€ |     28.160€ |
      +------------------------------------+----------+-----------+-------------+
      | Pneumatic Tubing                   |        7 |  1.191€/m |      8.337€ |
      +------------------------------------+----------+-----------+-------------+
      | Switch                             |        4 |    6.770€ |     27.080€ |
      +------------------------------------+----------+-----------+-------------+
      | Insulating Tape                    |        3 | 0.0645€/m |      0.193€ |
      +------------------------------------+----------+-----------+-------------+
      | **Total Cost**                                            |    104.675€ |
      +------------------------------------+----------+-----------+-------------+

   .. tabularcolumns:: |l|c|c|c|
   .. table::

      +------------------------------------+----------+-----------+-------------+
      | Cable Routing 5M - Bill of Materials                                    |
      +------------------------------------+----------+-----------+-------------+
      | Item                               | Quantity | Price/Pcs | Total Price |
      +====================================+==========+===========+=============+
      | Cam Lock 15mm x 12.5mm             |       20 |    0.148€ |      2.960€ |
      +------------------------------------+----------+-----------+-------------+
      | Cam Bolt 6mm x 45.5mm              |       10 |    0.880€ |      8.800€ |
      +------------------------------------+----------+-----------+-------------+
      | Wooden Dowel Pin 8mm x 30mm        |       15 |    0.029€ |      0.435€ |
      +------------------------------------+----------+-----------+-------------+
      | Melamine 18mm                      |    0.555 | 6.718€/m2 |      3.728€ |
      +------------------------------------+----------+-----------+-------------+
      | Electric Plugs                     |       10 |    2.790€ |     27.900€ |
      +------------------------------------+----------+-----------+-------------+
      | Electric Cable                     |        9 |  0.835€/m |      7.515€ |
      +------------------------------------+----------+-----------+-------------+
      | Pneumatic Coupling                 |       10 |    3.520€ |     35.200€ |
      +------------------------------------+----------+-----------+-------------+
      | Pneumatic Tubing                   |        9 |  1.191€/m |     10.720€ |
      +------------------------------------+----------+-----------+-------------+
      | Switch                             |        5 |    6.770€ |     33.850€ |
      +------------------------------------+----------+-----------+-------------+
      | Insulating Tape                    |        3 | 0.0645€/m |      0.193€ |
      +------------------------------------+----------+-----------+-------------+
      | **Total Cost**                                            |    131.302€ |
      +------------------------------------+----------+-----------+-------------+

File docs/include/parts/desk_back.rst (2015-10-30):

:index:`Desk Back`
------------------

OpenDeskLab can be configured with either a tall back or a short one. The tall back provides support for embedded lighting and connection to the room ventilation system, while the short back only goes up to the :doc:`cable_routing` height, allowing the user (and the superviser) to have visual contact with the installed facilities.

.. warning::

   In some countries it may be against the regulations to install a short back for safety reasons. It is up to the builder to choose the correct version if safety rules must apply.

The width of the back depends on the number of modules that the desk will be comprised. The assembly procedure however remains the same, although more bolts, locks and dowel pins are needed in the bigger desks.

.. important::

   Tools Needed:
    - Pozidriv Screwdriver

Tall back
^^^^^^^^^

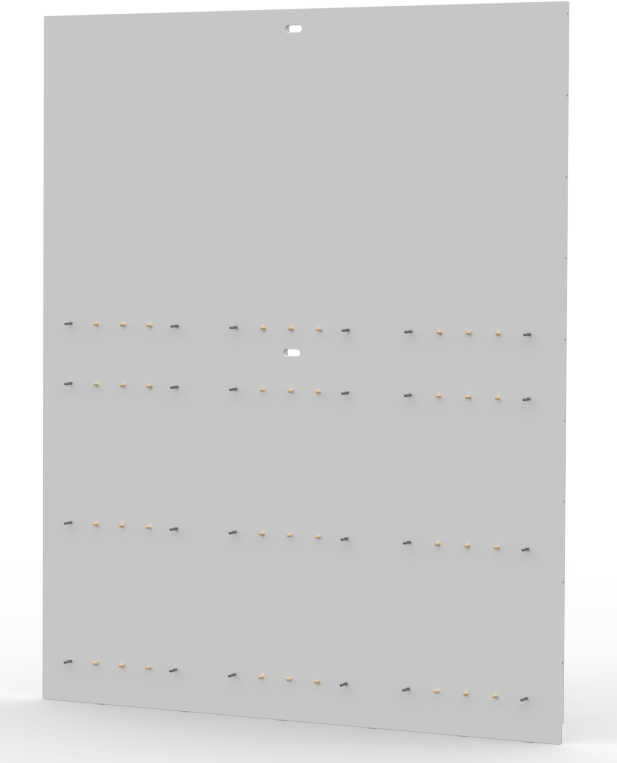
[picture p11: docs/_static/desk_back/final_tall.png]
desk back tall


Assembly Procedure
++++++++++++++++++

To assemble the back panel of the desk, all you have to do is insert the Cam Bolts, the Wooden Dowel Pins and the Cam Locks (without locking them).

.. raw:: html 

   <video src="../../_static/desk_back/Desk_Back_3M.ogv" width="696" type="video/ogg" controls="controls">
   Your browser does not support the video tag.
   </video>

Drawings
++++++++

Drawings are provided for the three module-wide version, for the other versions nothing changes besides the overall length of the module.

:download:`Tall Desk Back 3M </_static/desk_back/Desk_Back_3M.pdf>`

Bill of Materials
+++++++++++++++++

   .. tabularcolumns:: |l|c|c|c|
   .. table::

      +--------------------------------------+----------+-----------+-------------+
      | Tall Desk Back 3M - Bill of Materials                                     |
      +--------------------------------------+----------+-----------+-------------+
      | Item                                 | Quantity | Price/Pcs | Total Price |
      +======================================+==========+===========+=============+
      | Cam Lock 15mm x 12.5mm               |    24    |    0.148€ |      3.552€ |
      +--------------------------------------+----------+-----------+-------------+
      | Cam Bolt 6mm x 45.5mm                |    24    |    0.880€ |     21.120€ |
      +--------------------------------------+----------+-----------+-------------+
      | Wooden Dowel Pin 8mm x 30mm          |    36    |    0.029€ |      1.044€ |
      +--------------------------------------+----------+-----------+-------------+
      | Melamine 25mm                        |  2.745   | 8.958€/m2 |     24.590€ |
      +--------------------------------------+----------+-----------+-------------+
      | **Total Cost**                                              |     50.306€ |
      +--------------------------------------+----------+-----------+-------------+

   .. tabularcolumns:: |l|c|c|c|
   .. table::

      +--------------------------------------+----------+-----------+-------------+
      | Tall Desk Back 4M - Bill of Materials                                     |
      +--------------------------------------+----------+-----------+-------------+
      | Item                                 | Quantity | Price/Pcs | Total Price |
      +======================================+==========+===========+=============+
      | Cam Lock 15mm x 12.5mm               |    26    |    0.148€ |      3.848€ |
      +--------------------------------------+----------+-----------+-------------+
      | Cam Bolt 6mm x 45.5mm                |    32    |    0.880€ |     28.160€ |
      +--------------------------------------+----------+-----------+-------------+
      | Wooden Dowel Pin 8mm x 30mm          |    48    |    0.029€ |      1.392€ |
      +--------------------------------------+----------+-----------+-------------+
      | Melamine 25mm                        |  3.660   | 8.958€/m2 |     32.786€ |
      +--------------------------------------+----------+-----------+-------------+
      | **Total Cost**                                              |     66.186€ |
      +--------------------------------------+----------+-----------+-------------+

   .. tabularcolumns:: |l|c|c|c|
   .. table::

      +--------------------------------------+----------+-----------+-------------+
      | Tall Desk Back 5M - Bill of Materials                                     |
      +--------------------------------------+----------+-----------+-------------+
      | Item                                 | Quantity | Price/Pcs | Total Price |
      +======================================+==========+===========+=============+
      | Cam Lock 15mm x 12.5mm               |    28    |    0.148€ |      4.144€ |
      +--------------------------------------+----------+-----------+-------------+
      | Cam Bolt 6mm x 45.5mm                |    40    |    0.880€ |     35.200€ |
      +--------------------------------------+----------+-----------+-------------+
      | Wooden Dowel Pin 8mm x 30mm          |    60    |    0.029€ |      1.740€ |
      +--------------------------------------+----------+-----------+-------------+
      | Melamine 25mm                        |  4.575   | 8.958€/m2 |     40.983€ |
      +--------------------------------------+----------+-----------+-------------+
      | **Total Cost**                                              |     82.067€ |
      +--------------------------------------+----------+-----------+-------------+

Short back
^^^^^^^^^^

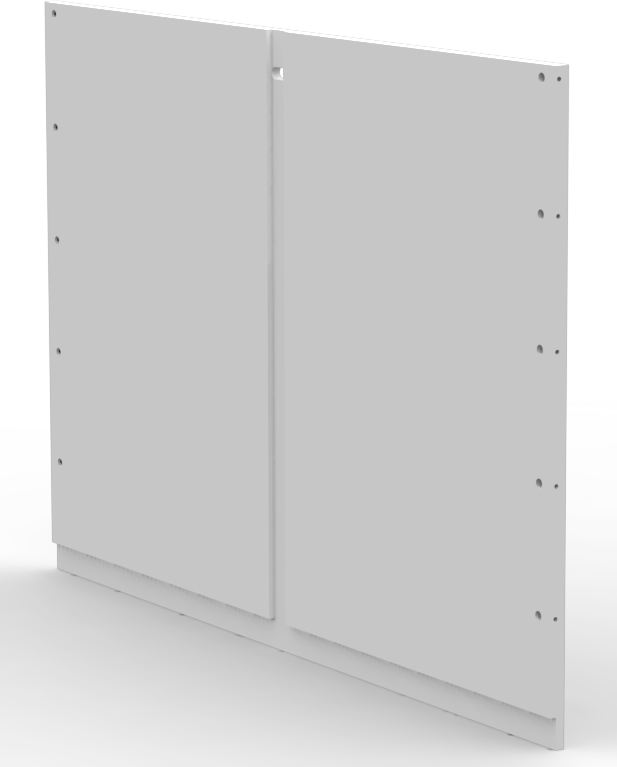
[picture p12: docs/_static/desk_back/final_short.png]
desk back short


Assembly Procedure
++++++++++++++++++

The procedure for the short back is the same as the tall one, only fewer components are needed.

Drawings
++++++++

Drawings are provided for the three module-wide version, for the other versions nothing changes besides the overall length of the module.

:download:`Short Desk Back 3M </_static/desk_back/Desk_Low_Back_3M.pdf>`

Bill of Materials
+++++++++++++++++

   .. tabularcolumns:: |l|c|c|c|
   .. table::

      +--------------------------------------+----------+-----------+-------------+
      | Short Desk Back 3M - Bill of Materials                                    |
      +--------------------------------------+----------+-----------+-------------+
      | Item                                 | Quantity | Price/Pcs | Total Price |
      +======================================+==========+===========+=============+
      | Cam Lock 15mm x 12.5mm               |    16    |    0.148€ |      2.368€ |
      +--------------------------------------+----------+-----------+-------------+
      | Cam Bolt 6mm x 45.5mm                |    24    |    0.880€ |     21.120€ |
      +--------------------------------------+----------+-----------+-------------+
      | Wooden Dowel Pin 8mm x 30mm          |    36    |    0.029€ |      1.044€ |
      +--------------------------------------+----------+-----------+-------------+
      | Melamine 25mm                        |  1.530   | 8.958€/m2 |     13.705€ |
      +--------------------------------------+----------+-----------+-------------+
      | **Total Cost**                                              |     38.238€ |
      +--------------------------------------+----------+-----------+-------------+

   .. tabularcolumns:: |l|c|c|c|
   .. table::

      +--------------------------------------+----------+-----------+-------------+
      | Short Desk Back 4M - Bill of Materials                                    |
      +--------------------------------------+----------+-----------+-------------+
      | Item                                 | Quantity | Price/Pcs | Total Price |
      +======================================+==========+===========+=============+
      | Cam Lock 15mm x 12.5mm               |    18    |    0.148€ |      2.664€ |
      +--------------------------------------+----------+-----------+-------------+
      | Cam Bolt 6mm x 45.5mm                |    32    |    0.880€ |     28.160€ |
      +--------------------------------------+----------+-----------+-------------+
      | Wooden Dowel Pin 8mm x 30mm          |    48    |    0.029€ |      1.392€ |
      +--------------------------------------+----------+-----------+-------------+
      | Melamine 25mm                        |  2.040   | 8.958€/m2 |     18.274€ |
      +--------------------------------------+----------+-----------+-------------+
      | **Total Cost**                                              |     50.490€ |
      +--------------------------------------+----------+-----------+-------------+

   .. tabularcolumns:: |l|c|c|c|
   .. table::

      +--------------------------------------+----------+-----------+-------------+
      | Short Desk Back 5M - Bill of Materials                                    |
      +--------------------------------------+----------+-----------+-------------+
      | Item                                 | Quantity | Price/Pcs | Total Price |
      +======================================+==========+===========+=============+
      | Cam Lock 15mm x 12.5mm               |    20    |    0.148€ |      2.960€ |
      +--------------------------------------+----------+-----------+-------------+
      | Cam Bolt 6mm x 45.5mm                |    40    |    0.880€ |     35.200€ |
      +--------------------------------------+----------+-----------+-------------+
      | Wooden Dowel Pin 8mm x 30mm          |    60    |    0.029€ |      1.740€ |
      +--------------------------------------+----------+-----------+-------------+
      | Melamine 25mm                        |  2.550   | 8.958€/m2 |     22.843€ |
      +--------------------------------------+----------+-----------+-------------+
      | **Total Cost**                                              |     62.743€ |
      +--------------------------------------+----------+-----------+-------------+

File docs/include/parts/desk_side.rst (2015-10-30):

:index:`Desk Side`
------------------

Depending on the :doc:`desk_back` configuration, the side panels also differentiate accordingly, with two different versions, a tall and a short one.

.. important::
   
   Tools Needed:
    - Pozidriv Screwdriver

Tall side
^^^^^^^^^

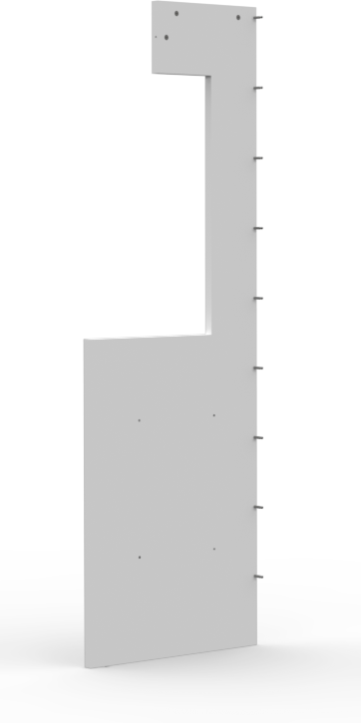
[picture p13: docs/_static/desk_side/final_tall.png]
desk side tall


Assembly Procedure
~~~~~~~~~~~~~~~~~~

The assembly procedure is fairly simple, just screw in the Cam Bolts and insert the Dowel Pins on the melamine board. The Cam Lock can also be inserted without however locking them in place.

.. raw:: html 

   <video src="../../_static/desk_side/Desk_Side_Left.ogv" width="696" type="video/ogg" controls="controls">
   Your browser does not support the video tag.
   </video>

Drawings
~~~~~~~~

Drawings are provided for the left melamine side, the right side is changed accordingly.

:download:`Tall Desk Side </_static/desk_side/Desk_Side_Left.pdf>`

Bill of Materials
~~~~~~~~~~~~~~~~~

   .. tabularcolumns:: |l|c|c|c|
   .. table::

      +--------------------------------------+----------+-----------+-------------+
      | Tall Desk Side - Bill of Materials (For both side panels)                 |
      +--------------------------------------+----------+-----------+-------------+
      | Item                                 | Quantity | Price/Pcs | Total Price |
      +======================================+==========+===========+=============+
      | Cam Lock 15mm x 12.5mm               |     6    |    0.148€ |      0.888€ |
      +--------------------------------------+----------+-----------+-------------+
      | Cam Bolt 6mm x 45.5mm                |    18    |    0.880€ |     15.840€ |
      +--------------------------------------+----------+-----------+-------------+
      | M6 x 40 Connecting Screws            |     4    |    0.753€ |      3.012€ |
      +--------------------------------------+----------+-----------+-------------+
      | Melamine 25mm                        | 1.530    | 8.958€/m2 |     13.710€ |
      +--------------------------------------+----------+-----------+-------------+
      | **Total Cost**                                              |     33.450€ |
      +--------------------------------------+----------+-----------+-------------+

Short side
^^^^^^^^^^

desk side short

Assembly Procedure
~~~~~~~~~~~~~~~~~~

The short side module is also very simple to assemble, fewer components are needed than the taller version.

Drawings
~~~~~~~~

Drawings are provided for the left melamine side, the right side is changed accordingly.

:download:`Short Desk Side </_static/desk_side/Desk_Side_Low_Left.pdf>`

Bill of Materials
~~~~~~~~~~~~~~~~~

   .. tabularcolumns:: |l|c|c|c|
   .. table::

      +--------------------------------------+----------+-----------+-------------+
      | Short Desk Side - Bill of Materials (For both side panels)                |
      +--------------------------------------+----------+-----------+-------------+
      | Item                                 | Quantity | Price/Pcs | Total Price |
      +======================================+==========+===========+=============+
      | Cam Bolt 6mm x 45.5mm                |    10    |    0.880€ |      8.800€ |
      +--------------------------------------+----------+-----------+-------------+
      | M6 x 40 Connecting Screws            |     4    |    0.753€ |      3.012€ |
      +--------------------------------------+----------+-----------+-------------+
      | Melamine 25mm                        | 1.167    | 8.958€/m2 |     10.454€ |
      +--------------------------------------+----------+-----------+-------------+
      | **Total Cost**                                              |     22.266€ |
      +--------------------------------------+----------+-----------+-------------+

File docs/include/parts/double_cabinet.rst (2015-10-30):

:index:`Double Cabinet`
-----------------------

double cabinet

The double cabinet is a double module for the OpenDeskLab. It is comprised of the five melamine boards that form the frame and the two melamine doors. 

The hinges are standardized and all the holes can be predrilled in the CNC mill of the melamine supplier.

.. important::

    Tools Needed:
     - Pozidriv Screwdriver
     - Electric Screwdriver for the six plastic legs

Assembly Procedure
~~~~~~~~~~~~~~~~~~

The assembly procedure is very simple, first you assemble the two side panels using the Cam Bolts and the Wooden Dowel Pins, and then you mount the Hinge Mounting Plates on the left and the right side panels.

.. raw:: html 

   <video src="../../_static/side_panel_assembly.ogv" width="696" type="video/ogg" controls="controls">
   Your browser does not support the video tag.
   </video>

Then you create the door assemblies by mounting the Concealed Hinges with the provided screws (3.5mm x 16mm) and lastly you screw in the Knobs.

.. raw:: html 

   <video src="../../_static/door_assembly.ogv" width="696" type="video/ogg" controls="controls">
   Your browser does not support the video tag.
   </video>

After you have assembled both sides and the door assemblies you can proceed to the next step. Attach the three Melamine parts on one of the side panels and then carefully align the second side panel on the assembly. After that, screw in the Cam Locks to secure the subassembly. Lie the subassembly down and screw in the six plastic legs on the bottom of the cabinet. Lastly, attach the already assembled doors on the cabinet by attaching the Concealed Hinges on their respective Hinge Mounting Plates and screw them in.

.. raw:: html 

   <video src="../../_static/double_cabinet/double_cabinet.ogv" width="696" type="video/ogg" controls="controls">
   Your browser does not support the video tag.
   </video>

Drawings
~~~~~~~~

:download:`Shelf </_static/double_cabinet/Double_Melamine_Shelf.pdf>`

:download:`Door </_static/single_cabinet/Melamine_Door.pdf>`

:download:`Side </_static/single_cabinet/Melamine_Side.pdf>`

:download:`Double Cabinet </_static/double_cabinet/Double_Cabinet.pdf>`

Bill of Materials
~~~~~~~~~~~~~~~~~

    .. tabularcolumns:: |l|c|c|c|
    .. table::

        +------------------------------------+----------+-----------+-------------+
        | Double Cabinet - Bill of Materials                                      | 
        +------------------------------------+----------+-----------+-------------+
        | Item                               | Quantity | Price/Pcs | Total Price |
        +====================================+==========+===========+=============+
        | Cam Lock 15mm x 12.5mm             |    24    |    0.148€ |      3.552€ |
        +------------------------------------+----------+-----------+-------------+
        | Cam Bolt 6mm x 45.5mm              |    12    |    0.880€ |     10.560€ |
        +------------------------------------+----------+-----------+-------------+
        | Wooden Dowel Pin 8mm x 30mm        |    18    |    0.029€ |      0.522€ |
        +------------------------------------+----------+-----------+-------------+
        | Concealed Hinge (9mm Overlay)      |     4    |    1.690€ |      6.760€ |
        +------------------------------------+----------+-----------+-------------+
        | Hinge Mounting Plate               |     4    |    0.980€ |      3.920€ |
        +------------------------------------+----------+-----------+-------------+
        | Plastic Adjustable Legs 100mm      |     6    |    0.750€ |      4.500€ |
        +------------------------------------+----------+-----------+-------------+
        | M6 x 40 Connecting Screws          |     4    |    0.753€ |      3.012€ |
        +------------------------------------+----------+-----------+-------------+
        | Melamine 18mm                      |  3.228   | 6.718€/m2 |     21.691€ |
        +------------------------------------+----------+-----------+-------------+
        | Door Knob                          |     2    |    1.080€ |      2.160€ |
        +------------------------------------+----------+-----------+-------------+
        | **Total Cost**                                            |     56.677€ |
        +------------------------------------+----------+-----------+-------------+

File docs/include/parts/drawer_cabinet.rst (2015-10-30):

:index:`Drawer Cabinet`
-----------------------

drawer cabinet

The drawer cabinet is a single module for the OpenDeskLab. It is comprised of a drawer and a small cabinet.

.. important::

   Tools Needed:
    - Pozidriv Screwdriver
    - Electric Screwdriver for the four plastic legs

Assembly Procedure
~~~~~~~~~~~~~~~~~~

First you assemble the drawer, which is comprised of two side panels, one bottom panel, one back panel and the front drawer panel.

.. raw:: html 

   <video src="../../_static/drawer_cabinet/Drawer.ogv" width="696" type="video/ogg" controls="controls">
   Your browser does not support the video tag.
   </video>

Then you assemble the rest of the cabinet the same way the :doc:`single_cabinet` and the :doc:`double_cabinet` are assembled.

.. raw:: html 

   <video src="../../_static/drawer_cabinet/Drawer_Cabinet.ogv" width="696" type="video/ogg" controls="controls">
   Your browser does not support the video tag.
   </video>

Drawings
~~~~~~~~

:download:`Drawer </_static/drawer_cabinet/Drawer.pdf>`

:download:`Drawer Left Side </_static/drawer_cabinet/Drawer_Melamine_Left_Side.pdf>`

:download:`Drawer Door </_static/drawer_cabinet/Drawer_Door.pdf>`

:download:`Drawer Cabinet </_static/drawer_cabinet/Drawer_Cabinet.pdf>`

:download:`Drawer Shelf </_static/single_cabinet/Melamine_Shelf.pdf>`

Bill of Materials
~~~~~~~~~~~~~~~~~

   .. tabularcolumns:: |l|c|c|c|
   .. table::

      +------------------------------------+----------+-----------+-------------+
      | Drawer Cabinet - Bill of Materials                                      | 
      +------------------------------------+----------+-----------+-------------+
      | Item                               | Quantity | Price/Pcs | Total Price |
      +====================================+==========+===========+=============+
      | Cam Lock 15mm x 12.5mm             |    30    |    0.148€ |      4.440€ |
      +------------------------------------+----------+-----------+-------------+
      | Cam Bolt 6mm x 45.5mm              |    24    |    0.880€ |     21.120€ |
      +------------------------------------+----------+-----------+-------------+
      | Wooden Dowel Pin 8mm x 30mm        |    18    |    0.029€ |      0.522€ |
      +------------------------------------+----------+-----------+-------------+
      | Concealed Hinge (9mm Overlay)      |     2    |    1.690€ |      3.380€ |
      +------------------------------------+----------+-----------+-------------+
      | Hinge Mounting Plate               |     2    |    0.980€ |      1.960€ |
      +------------------------------------+----------+-----------+-------------+
      | Plastic Adjustable Legs 100mm      |     4    |    0.750€ |      3.000€ |
      +------------------------------------+----------+-----------+-------------+
      | M6 x 40 Connecting Screws          |     4    |    0.753€ |      3.012€ |
      +------------------------------------+----------+-----------+-------------+
      | Melamine 18mm                      |  2.432   | 6.718€/m2 |     16.341€ |
      +------------------------------------+----------+-----------+-------------+
      | Door Knob                          |     2    |    1.080€ |      2.160€ |
      +------------------------------------+----------+-----------+-------------+
      | **Total Cost**                                            |     55.935€ |
      +------------------------------------+----------+-----------+-------------+

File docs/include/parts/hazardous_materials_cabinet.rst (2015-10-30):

:index:`Hazardous Materials Cabinet`
------------------------------------

hazardous materials cabinet

The hazardous materials cabinet is a single module for the OpenDeskLab. It is very similar to the :doc:`single_cabinet` module, but it is made of plywood and it includes a back panel that protects it's contents. The shelves have a front cover that prevents accidents from spillage.

The sides of the frame can be used to mount the door either as right swing or as left swing, with no modifications on the frame or the door itself. The hinges are standardized and all the holes can be predrilled in the CNC mill of the plywood supplier.

.. warning::
   The Hazardous Materials Cabinet is **not** fireproof. This cabinet is designed to keep flames away from your flammables for 10 minutes so you have time to escape a fire.

.. important::

   Tools Needed:
    - Pozidriv Screwdriver
    - Electric Screwdriver for the four metal legs
    - Paint Brush

Assembly Procedure
++++++++++++++++++

The hazardous materials cabinet must be carefully assembled to provide the required protection. After the carefull assembly of the cabinet, before connecting the door, the silicone caulk must be used to provide an airtight seal when closed. The hinges used for this cabinet **should** be self-closing.

This cabinet is the only one that must be painted, using a special fire-retardant paint. You should paint the panels before assembling them together, since after the assembly it can be very difficult to paint everything evenly.

First you assemble the side panels

.. raw:: html 

   <video src="../../_static/side_panel_assembly.ogv" width="696" type="video/ogg" controls="controls">
   Your browser does not support the video tag.
   </video>

Then you assemble the door

.. raw:: html 

   <video src="../../_static/door_assembly.ogv" width="696" type="video/ogg" controls="controls">
   Your browser does not support the video tag.
   </video>

And you combine them all together

.. raw:: html 

   <video src="../../_static/hazardous_materials_cabinet/Hazardous_Materials_Cabinet.ogv" width="696" type="video/ogg" controls="controls">
   Your browser does not support the video tag.
   </video>

Drawings
++++++++

:download:`Side </_static/hazardous_materials_cabinet/Hazardous_Side_Panel.pdf>`

:download:`Shelf </_static/hazardous_materials_cabinet/Hazardous_Shelf.pdf>`

:download:`Lip </_static/hazardous_materials_cabinet/Hazardous_Lip.pdf>`

:download:`Back Panel </_static/hazardous_materials_cabinet/Hazardous_Back_Panel.pdf>`

:download:`Door </_static/single_cabinet/Melamine_Door.pdf>`

:download:`Hazardous Materials Cabinet </_static/hazardous_materials_cabinet/Hazardous_Materials_Cabinet.pdf>`

Bill of Materials
+++++++++++++++++

   .. tabularcolumns:: |l|c|c|c|
   .. table::
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

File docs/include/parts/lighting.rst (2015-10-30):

:index:`Lighting and Ventilation`
---------------------------------

single cabinet

The lighting module connects on the tall :doc:`desk_back` module and provides lighting to the worktop using a LED stripe. The LED stripe can be turned on and off using the switch that is attached on the :doc:`cable_routing` module.

The lighting module can be predrilled for ventilation installation. 

.. important::

    Tools Needed:
     - Pozidriv Screwdriver
     - Wire Cutter
     - Scissors

Assembly Procedure
++++++++++++++++++

First you assemble the top panel

.. raw:: html 

   <video src="../../_static/lighting/Lighting_Top_3M.ogv" width="696" type="video/ogg" controls="controls">
   Your browser does not support the video tag.
   </video>

Then you assemble the front panel

.. raw:: html 

   <video src="../../_static/lighting/Lighting_Front_3M.ogv" width="696" type="video/ogg" controls="controls">
   Your browser does not support the video tag.
   </video>

Lastly you attach them together

.. raw:: html 

   <video src="../../_static/lighting/Lighting_3M.ogv" width="696" type="video/ogg" controls="controls">
   Your browser does not support the video tag.
   </video>

Drawings
++++++++
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

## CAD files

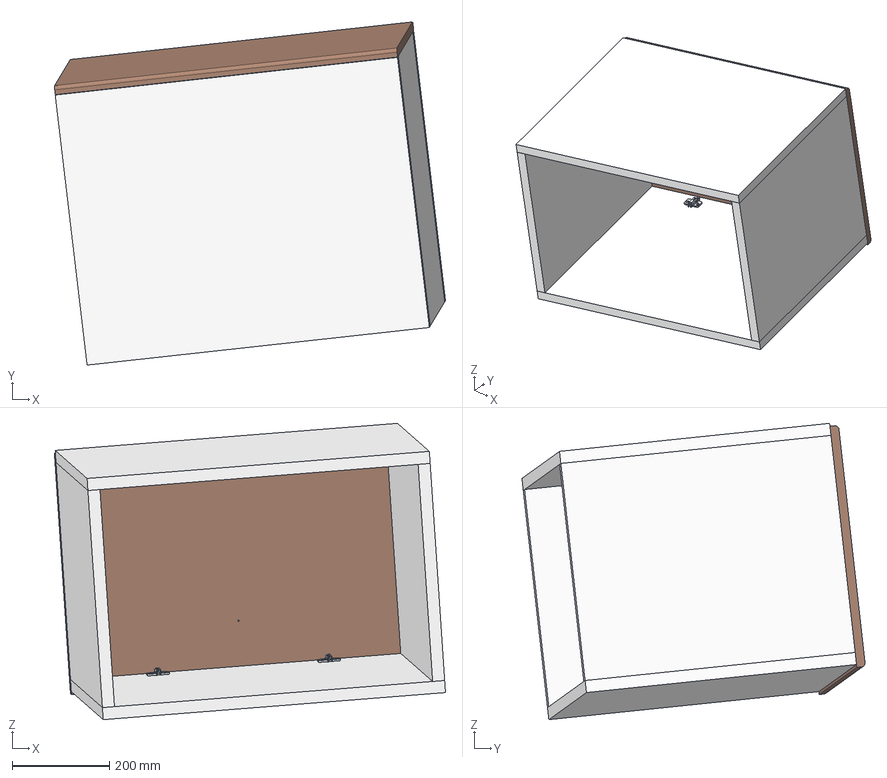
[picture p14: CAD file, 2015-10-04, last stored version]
CAD/single_cabinet/Single Cabinet with Hinges.stp
803.8 x 705.5 x 609.1 mm
inside left of modular x 2
230-P4W-32T_B x 4
230-P4W-32T_A x 4
door
230-26_19T_A x 2
230-26_19T_B x 2
230-26_19T_D x 2
230-26_19T_C x 2
modular up and down x 2

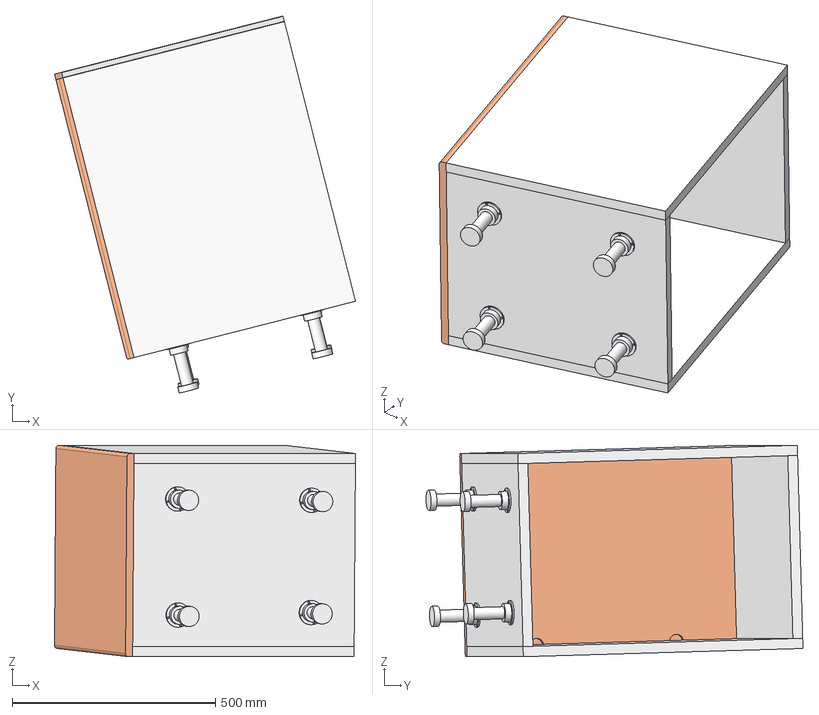
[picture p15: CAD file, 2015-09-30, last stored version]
CAD/single_cabinet/cabinet.stp
740.4 x 927.3 x 520.0 mm
modular up and down x 2
inside left of modular x 2
door
Leg x 4

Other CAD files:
CAD/single_cabinet/cabinet.dwg

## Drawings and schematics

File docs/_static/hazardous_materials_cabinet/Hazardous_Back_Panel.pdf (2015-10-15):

70 760 8

E E

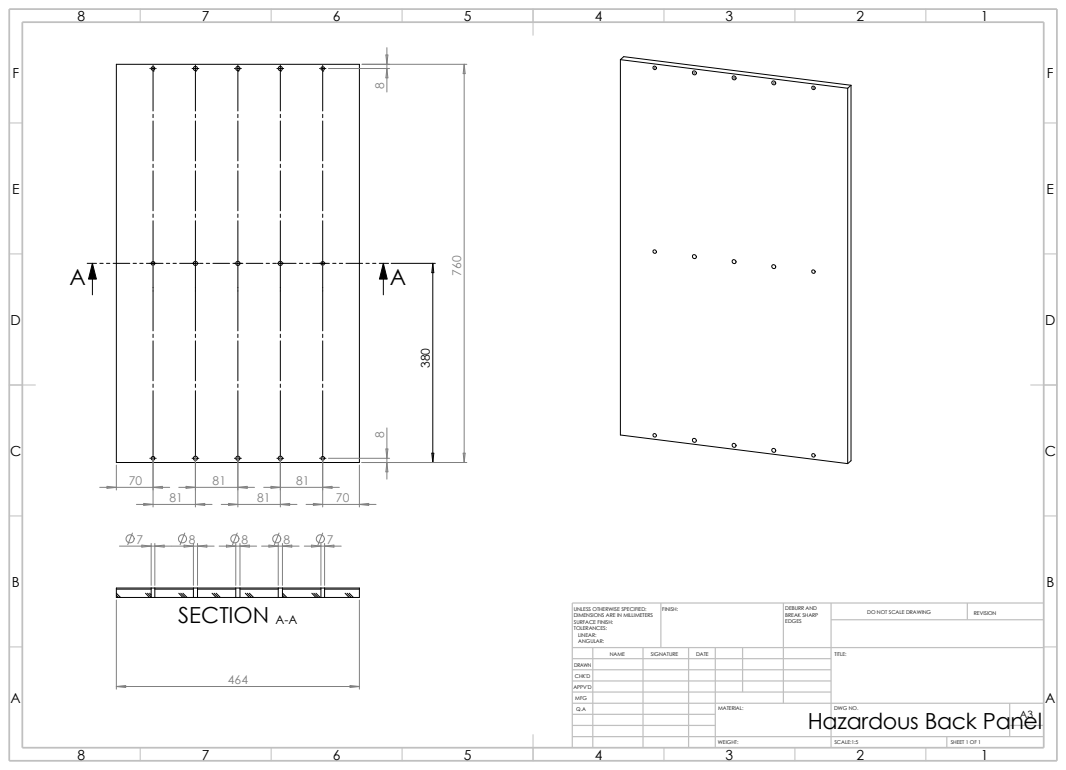
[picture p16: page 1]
WEIGHT:; SHEET 1 OF 1; SCALE:1:5; REVISION; FINISH:; EDGES; DEBURR AND BREAK SHARP; SECTION A-A

DO NOT SCALE DRAWING UNLESS OTHERWISE SPECIFIED:
DIMENSIONS ARE IN MILLIMETERS
SURFACE FINISH:
TOLERANCES:
LINEAR:
ANGULAR:

NAME | SIGNATURE | DATE | | | Hazardous Back Panel | TITLE:
DRAWN
CHK'D
APPV'D
MFG
Q.A | | | | MATERIAL: | DWG NO. | A3

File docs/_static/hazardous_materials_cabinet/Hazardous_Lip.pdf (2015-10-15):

E E

F F

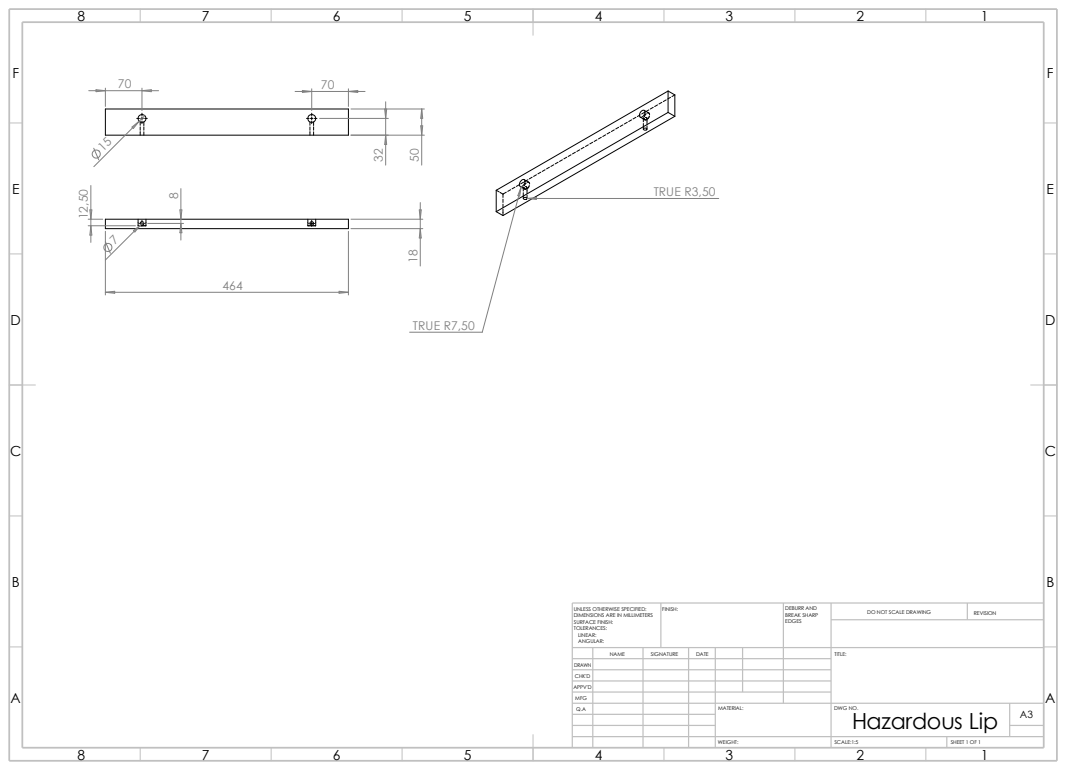
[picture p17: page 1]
SCALE:1:5; WEIGHT:; SHEET 1 OF 1; FINISH:; EDGES; DO NOT SCALE DRAWING; REVISION; DEBURR AND BREAK SHARP; TRUE R7,50; TRUE R3,50

Hazardous Lip ³² ¹⁵

UNLESS OTHERWISE SPECIFIED:
DIMENSIONS ARE IN MILLIMETERS
SURFACE FINISH:
TOLERANCES:
LINEAR:
ANGULAR:

NAME | SIGNATURE | DATE | | | | TITLE:
DRAWN
CHK'D
APPV'D
MFG
Q.A | | | | MATERIAL: | DWG NO. | A3

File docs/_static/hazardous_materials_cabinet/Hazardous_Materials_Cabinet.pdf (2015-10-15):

E E

F F

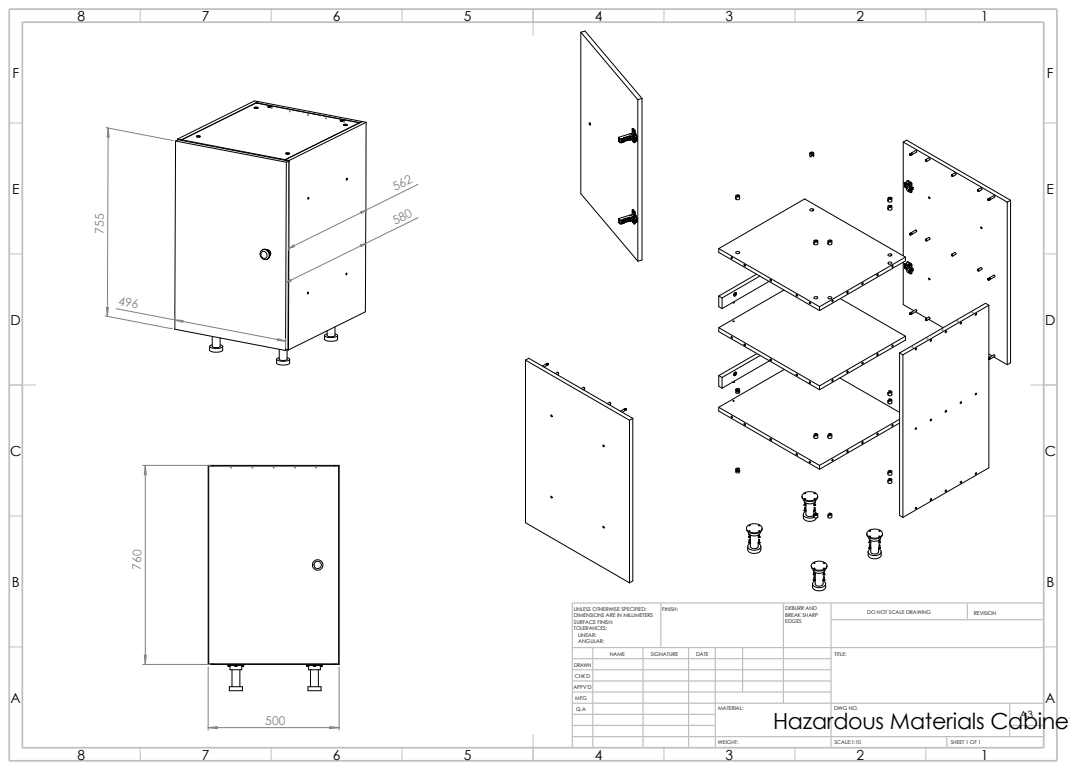
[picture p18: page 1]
WEIGHT:; SHEET 1 OF 1; SCALE:1:10; FINISH:; EDGES; DO NOT SCALE DRAWING; REVISION; DEBURR AND BREAK SHARP

Hazardous Materials Cabinet ⁷⁶⁰

UNLESS OTHERWISE SPECIFIED:
DIMENSIONS ARE IN MILLIMETERS
SURFACE FINISH:
TOLERANCES:
LINEAR:
ANGULAR:

NAME | SIGNATURE | DATE | | | | TITLE:
DRAWN
CHK'D
APPV'D
MFG
Q.A | | | | MATERIAL: | DWG NO. | A3

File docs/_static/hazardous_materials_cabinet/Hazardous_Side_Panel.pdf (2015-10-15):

B

E E

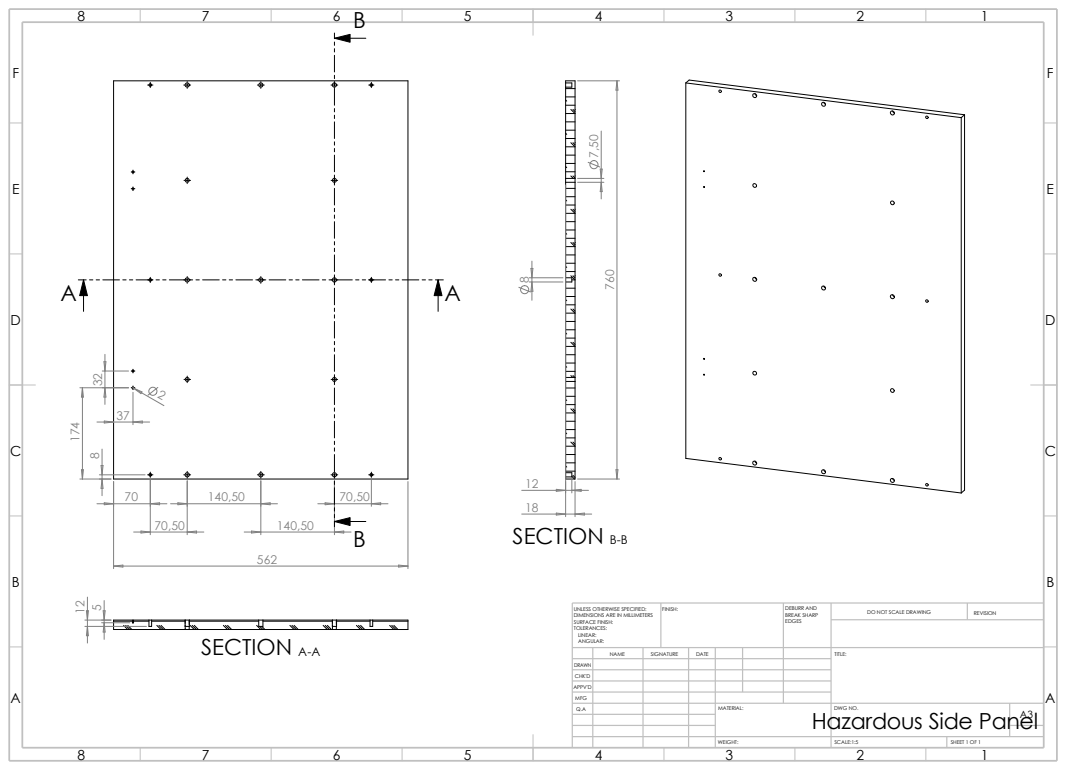
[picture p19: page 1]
70,50 ¹⁷⁴ ³² 37; SCALE:1:5; WEIGHT:; SHEET 1 OF 1; FINISH:; EDGES; DO NOT SCALE DRAWING; REVISION; DEBURR AND BREAK SHARP; SECTION B-B; SECTION A-A ⁵ ¹²

UNLESS OTHERWISE SPECIFIED:
DIMENSIONS ARE IN MILLIMETERS
SURFACE FINISH:
TOLERANCES:
LINEAR:
ANGULAR:

NAME | SIGNATURE | DATE | | | Hazardous Side Panel | TITLE:
DRAWN
CHK'D
APPV'D
MFG
Q.A | | | | MATERIAL: | DWG NO. | A3

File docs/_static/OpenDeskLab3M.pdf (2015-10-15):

E E

F F

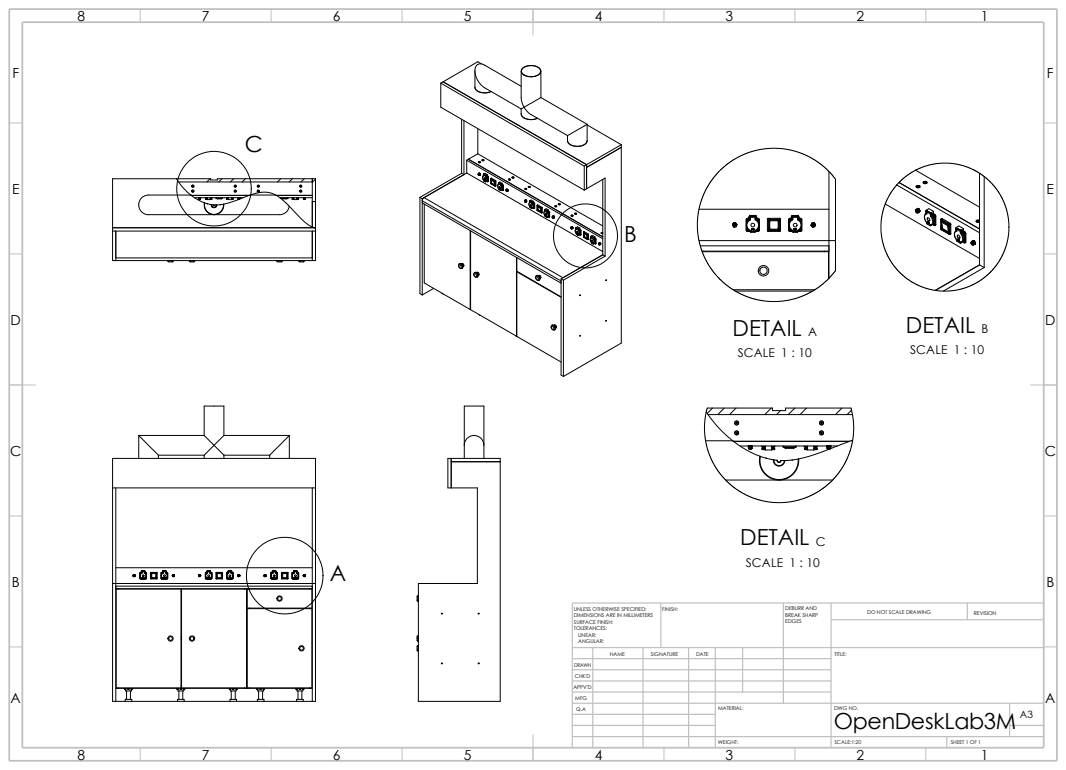
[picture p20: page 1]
DO NOT SCALE DRAWING; REVISION; SCALE:1:20; SHEET 1 OF 1; WEIGHT:; EDGES; UNLESS OTHERWISE SPECIFIED:; FINISH:; DEBURR AND BREAK SHARP; DETAIL B SCALE 1 : 10; DETAIL C SCALE 1 : 10; DETAIL A SCALE 1 : 10

DIMENSIONS ARE IN MILLIMETERS
SURFACE FINISH:
TOLERANCES:
LINEAR:
ANGULAR:

NAME | SIGNATURE | DATE | | | | TITLE: OpenDeskLab3M
DRAWN
CHK'D
APPV'D
MFG
Q.A | | | | MATERIAL: | DWG NO. | A3

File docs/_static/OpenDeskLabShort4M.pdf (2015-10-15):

A
E E

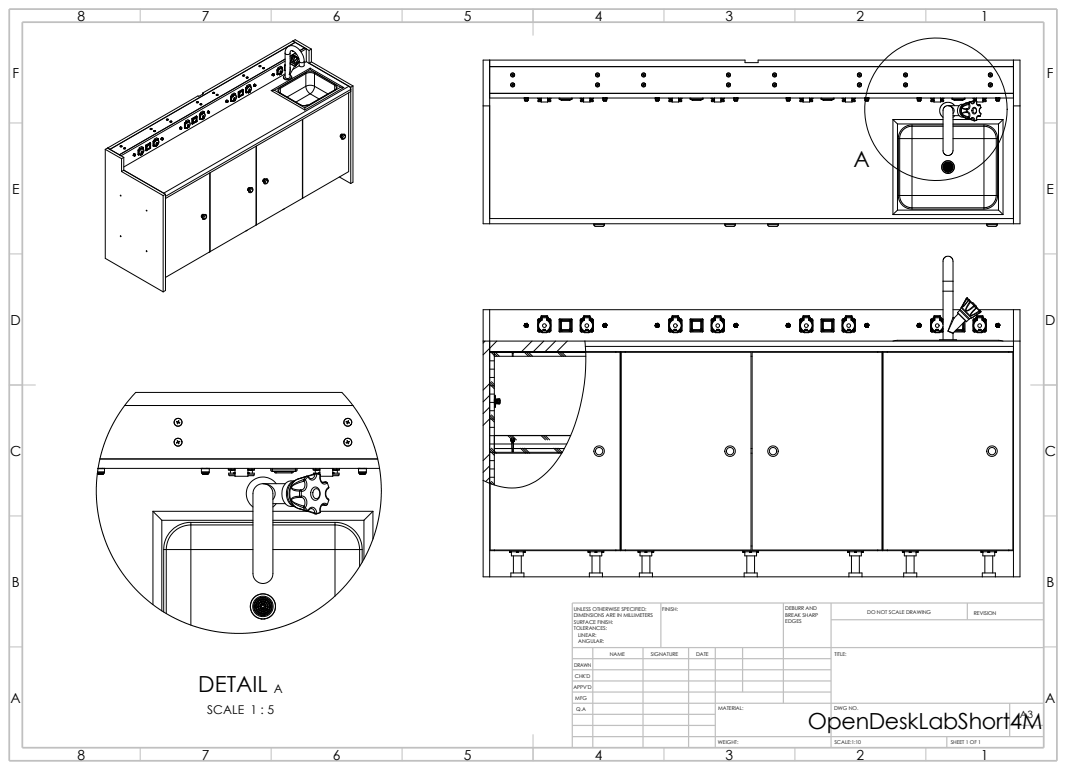
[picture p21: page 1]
TITLE:; SHEET 1 OF 1; WEIGHT:; SCALE:1:10; DO NOT SCALE DRAWING; REVISION; SIGNATURE; DATE DRAWN; FINISH:; EDGES; DEBURR AND BREAK SHARP OpenDeskLabShort4M; DETAIL A SCALE 1 : 5

UNLESS OTHERWISE SPECIFIED:
DIMENSIONS ARE IN MILLIMETERS
SURFACE FINISH:
TOLERANCES:
LINEAR:
ANGULAR:
NAME

CHK'D
APPV'D
MFG
Q.A | MATERIAL: | DWG NO. | A3

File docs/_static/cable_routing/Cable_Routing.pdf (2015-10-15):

E E

F F

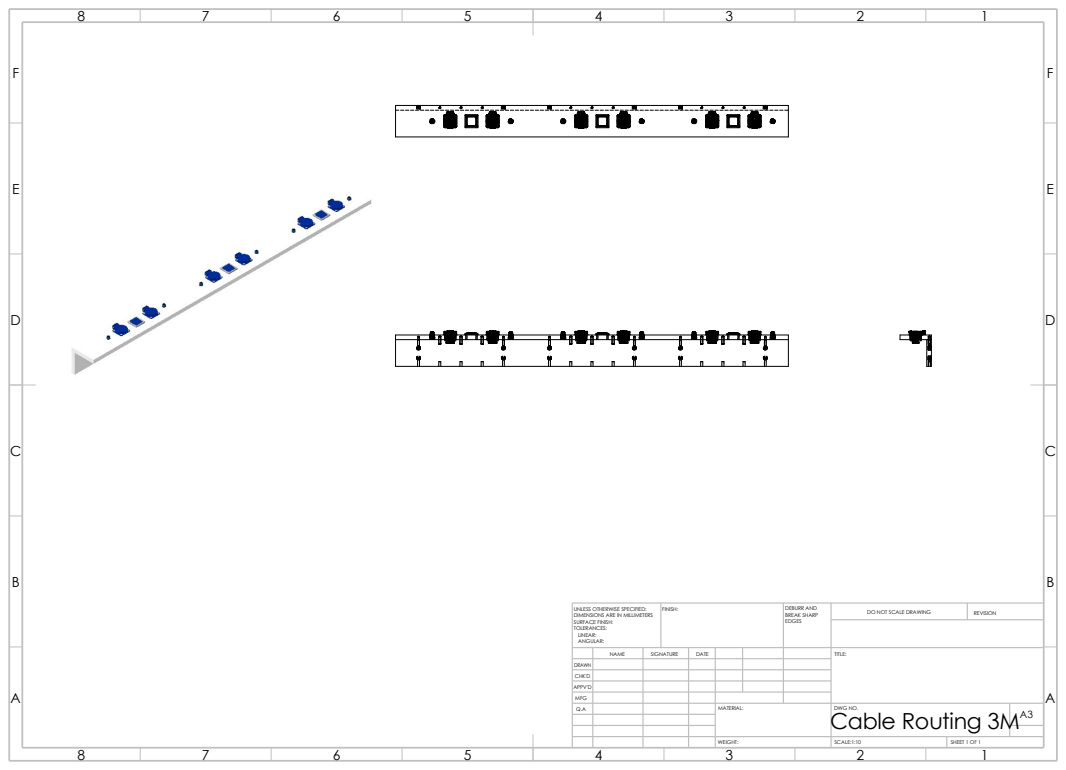
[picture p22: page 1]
WEIGHT:; SCALE:1:10; SHEET 1 OF 1; FINISH:; EDGES; DO NOT SCALE DRAWING; REVISION; DEBURR AND BREAK SHARP

UNLESS OTHERWISE SPECIFIED:
DIMENSIONS ARE IN MILLIMETERS
SURFACE FINISH:
TOLERANCES:
LINEAR:
ANGULAR:

NAME | SIGNATURE | DATE | | | | TITLE: Cable Routing 3M
DRAWN
CHK'D
APPV'D
MFG
Q.A | | | | MATERIAL: | DWG NO. | A3

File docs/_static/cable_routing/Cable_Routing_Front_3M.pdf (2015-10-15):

4,50

# 60 ¹²⁰

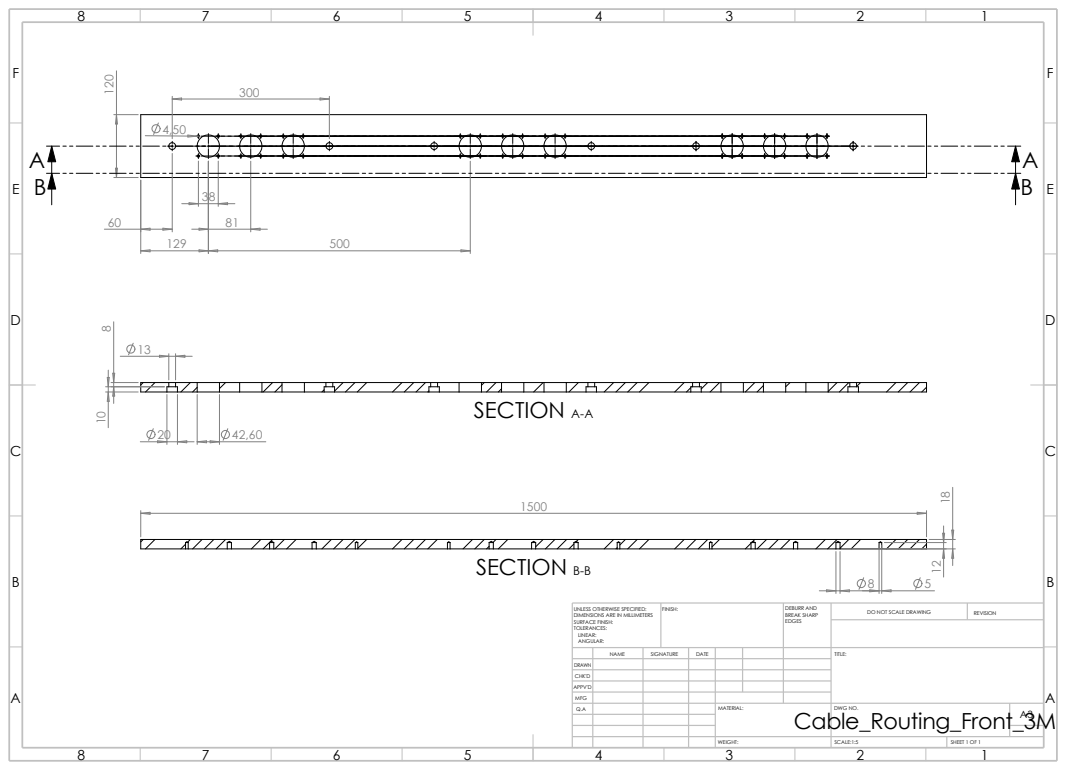
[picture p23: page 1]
SCALE:1:5; WEIGHT:; SHEET 1 OF 1; FINISH:; EDGES; DO NOT SCALE DRAWING; REVISION; DEBURR AND BREAK SHARP; SECTION A-A; SECTION B-B

UNLESS OTHERWISE SPECIFIED:
DIMENSIONS ARE IN MILLIMETERS
SURFACE FINISH:
TOLERANCES:
LINEAR:
ANGULAR:

NAME | SIGNATURE | DATE | | | Cable_Routing_Front_3Μ | TITLE:
DRAWN
CHK'D
APPV'D
MFG
Q.A | | | | MATERIAL: | DWG NO. | A3

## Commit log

2015-09-30 Added single cabinet files and rendering
    [cabinet.dwg, cabinet.stp]
2015-10-04 Updated single cabinet, developing double
    [Single Cabinet with Hinges.stp, cabinet.dwg, cabinet.stp]
2015-10-08 First test of uploading assembly video
2015-10-13 Modified Hazardous Materials Cabinet
2015-10-14 Adding new renders and final information
    [Single Cabinet with Hinges.stp]
2015-10-15 Finalized BOM of Cable Routing Module
2015-10-15 Fixed minor issue in cable routing, finalized BOM of Desk Back
2015-10-15 Finalized hazardous materials cabinet BOM
2015-10-15 Update Ταυτότητα Έργου.md
2015-10-30 Changed Philips screwdriver to Pozidriv

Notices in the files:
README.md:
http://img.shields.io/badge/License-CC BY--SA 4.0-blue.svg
